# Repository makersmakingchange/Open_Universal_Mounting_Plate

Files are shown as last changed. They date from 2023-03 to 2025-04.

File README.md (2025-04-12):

#  Open Universal Mounting Plate
The Open Universal Mounting Plate is a simple mounting option for assistive devices that do not have integrated mounting hardware. This device uses hook and loop fastener strips to attach to an assistive device allowing it to be mounted with standard ¼”-20 mounts, like those found on readily available camera mounting accessories.

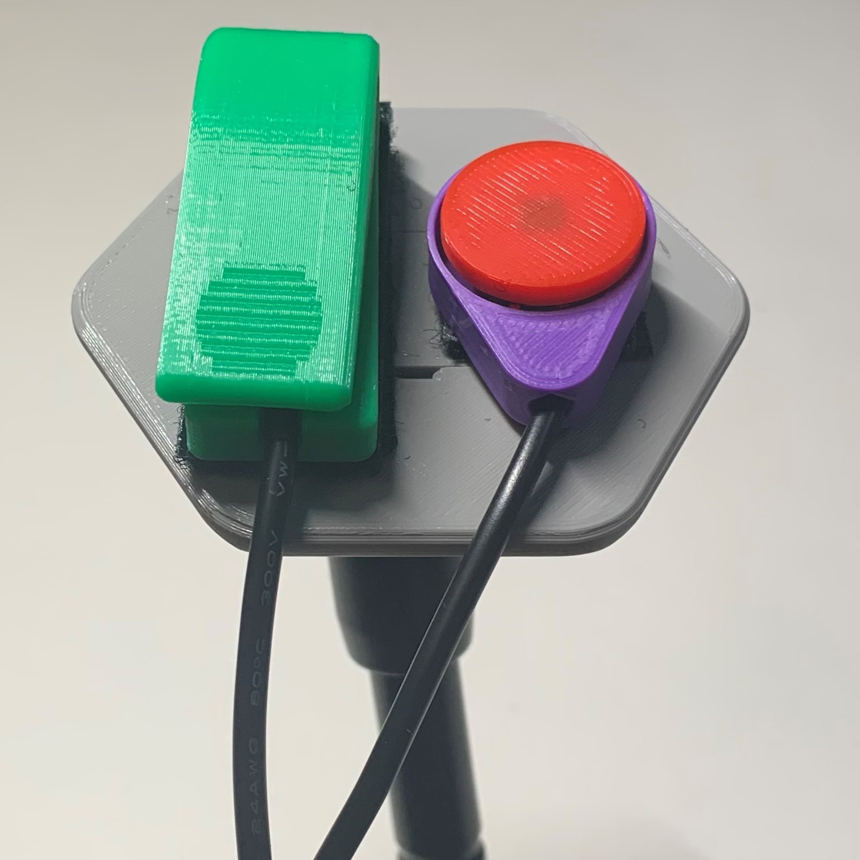
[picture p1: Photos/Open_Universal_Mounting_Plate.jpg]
A 3D printed hexagon mounting plate holding two assistive switches


## More info at
- [Makers Making Change Project Page](https://makersmakingchange.com/project/open-universal-mounting-plate)

## How to Obtain an Open Universal Mounting Plate
### 1. Do it Yourself (DIY) or Do it Together (DIT)

This is an open-source assistive technology, so anyone is free to build it. All of the files and instructions required to build the Open Universal Mounting Plate are contained within this repository. Refer to the Maker Checklist below.

### 2. Request a build of this device

If you would like to obtain an Open Universal Mounting Plate, you may submit a build request through the [MMC Library Page](https://makersmakingchange.com/project/open-universal-mounting-plate/). The requestor is responsible for the cost of materials and any shipping.

### 3. How to build this device for someone else

If you have the skills and equipment to build this device, and would like to donate your time to create the switch for someone who needs it, visit the [MMC Maker Wanted](https://makersmakingchange.com/maker-wanted/) section.

## Getting Started

### 1. Read the Makers Checklist

The Makers Checklist contains a list of tasks to complete to build the device.

### 2. Order the Off-The-Shelf Components

The [Bill of Materials](/Documentation/Open_Universal_Mounting_Plate_BOM.xlsx) lists all of the parts and components required to build the Open Universal Mounting Plate. The off-the-shelf components are are available online or may be available in smaller quantities at your local hardware store or dollar store.

### 3. Print the 3D Printable components

Refer to the [Sizing Chart](/Documentation/Open_Universal_Mounting_Plate_Sizing_Chart.pdf) to determine the correct configuration and corresponding print files.

All of the files and individual print files can be in the [/Build_Files/3D_Printing_Files](/Build_Files/3D_Printing_Files/) folder.

### 4. Assemble the Open Universal Mounting Plate...

Reference the [Assembly Guide](/Documentation/Open_Universal_Mounting_Plate_Assembly_Guide.pdf) for the tools and steps required to build each portion.

## Files
### Documentation
| Document             | Version | Link |
|----------------------|---------|------|
| Design Rationale     | 1.0     | [Open_Universal_Mounting_Plate_Design_Rationale](/Documentation/Open_Universal_Mounting_Plate_Design_Rationale.pdf)     |
| Maker Checklist      | 1.0     | [Open_Universal_Mounting_Plate_Maker_Checklist](/Documentation/Open_Universal_Mounting_Plate_Maker_Checklist.pdf)     |
| Bill of Materials    | 1.0     | [Open_Universal_Mounting_Plate_Bill_of_Materials](/Documentation/Open_Universal_Mounting_Plate_BOM.xlsx)     |
| 3D Printing Guide    | 1.0     | [Open_Universal_Mounting_Plate_3D_Printing_Guide](/Documentation/Open_Universal_Mounting_Plate_3D_Printing_Guide.pdf)     |
| Assembly Guide       | 1.0     | [Open_Universal_Mounting_Plate_Assembly_Guide](/Documentation/Open_Universal_Mounting_Plate_Assembly_Guide.pdf)     |
| User Guide           | 1.0     | [Open_Universal_Mounting_Plate_User_Guide](/Documentation/Open_Universal_Mounting_Plate_User_Guide.pdf)    |
| Sizing Chart         | 1.0     | [Open_Universal_Mounting_Plate_Sizing_Chart](/Documentation/Open_Universal_Mounting_Plate_Sizing_Chart.pdf)     |
| Changelog            | 1.0     | [Open_Universal_Mounting_Plate_Changelog](/Documentation/Open_Universal_Mounting_Plate_Changelog.pdf)     |

### Design Files
- [CAD Files](/Design_Files)

### Build Files
- [3D Printing Files](/Build_Files/3D_Printing_Files)

## Attribution

Design and documentation by Makers Making Change. 

## License
Everything needed or used to design, make, test, or prepare the Open Universal Mounting Plate is licensed under the CERN 2.0 Permissive license <https://ohwr.org/project/cernohl/wikis/Documents/CERN-OHL-version-2> (CERN-OHL-P) . 

Accompanying material such as instruction manuals, videos, and other copyrightable works that are useful but not necessary to design, make, test, or prepare the Open Universal Mounting Plate are published under a Creative Commons Attribution-ShareAlike 4.0 license https://creativecommons.org/licenses/by-sa/4.0/ (CC BY-SA 4.0).

---
<!-- ABOUT MMC START -->
## About Makers Making Change
[Makers Making Change Logo](https://www.makersmakingchange.com/)

Makers Making Change is a program of [Neil Squire](https://www.neilsquire.ca/), a Canadian non-profit that uses technology, knowledge, and passion to empower people with disabilities.

Makers Making Change leverages the capacity of community based Makers, Disability Professionals and Volunteers to develop and deliver affordable Open Source Assistive Technologies.

 - Website: [www.MakersMakingChange.com](https://www.makersmakingchange.com/)
 - GitHub: [makersmakingchange](https://github.com/makersmakingchange)
 - Bluesky: [@makersmakingchange.bsky.social](https://bsky.app/profile/makersmakingchange.bsky.social)
 - Instagram: [@makersmakingchange](https://www.instagram.com/makersmakingchange)
 - Facebook: [makersmakechange](https://www.facebook.com/makersmakechange)
 - LinkedIn: [Neil Squire Society](https://www.linkedin.com/company/neil-squire-society/)
 - Thingiverse: [makersmakingchange](https://www.thingiverse.com/makersmakingchange/about)
 - Printables: [MakersMakingChange](https://www.printables.com/@MakersMakingChange)

### Contact Us
For technical questions, to get involved, or to share your experience we encourage you to [visit our website](https://www.makersmakingchange.com/) or [contact us](https://www.makersmakingchange.com/s/contact).
<!-- ABOUT MMC END -->

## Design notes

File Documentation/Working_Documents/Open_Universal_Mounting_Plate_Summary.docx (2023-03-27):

Title

Open Universal Mounting Plate

Subtitle

A simple mounting option for AT that doesn’t have integrated mounting hardware.

## Device Specifications

Build Time:

< 1hr

1-4 hr

5-10hr

>10hr

Cost:

$0 - $10

$11 - $25

$26 - $50

$51 - $100

$101 - $250

$250+

Stage: Recently Added

Skills: 3D Printing

Need: Agility / Dexterity

Disability: Mobility / Physical

Difficulty: Beginner

License:

Usages:

Type:

Designer:

## Device Details

### Overview

The Open Universal Mounting Plate is a simple mounting option for assistive devices that do not have integrated mounting hardware. This device uses hook and loop fastener strips to attach to an assistive device allowing it to be mounted with standard ¼”-20 mounts, like those found on readily available camera mounting accessories.

### Sizing

This device has multiple options for both mounting plate size and tee nut length. If you are requesting this device, please let the builder know what options work best for you. Refer to the Sizing Chart for more information.

### Usage

Hook and loop fastener strips (Velcro) can be used to secure one or more devices to the mounting plate. A mounting system that uses ¼”-20 external threads can then me secured to the mounting and positioned for use.

### Cost

~

### Build Instructions

Refer to the Assembly Guide and 3D Printing Guide for detailed instructions.

#### Skills Required

This is a beginner level build that involves 3D printing and minor assembly.

#### Time Required

3D Printing Time: 1h24m to 4h14m (depending on plate size and tee nut length)

Assembly Time: 15m

#### Tools

- 3D Printer
- Small Flat Head Screwdriver
- Pliers

#### Components

- 1X Mounting Plate
- 1X Hardware Cover
- 1X Assembly Washer

### Attribution

Design and Documentation by Makers Making Change

© 2022 by <Author>. This work is licensed under the CC BY SA 4.0 License: http://creativecommons.org/licenses/by-sa/4.0 Files available at <Replace with MMC Library Link> Page 1 of 2

VX.X | <MONTH> <YEAR> <Device Name> Summary

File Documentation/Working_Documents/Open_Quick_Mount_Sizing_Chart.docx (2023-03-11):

# Introduction

The Hexagon Quick Mount is a simple mounting option for assistive devices that do not have integrated mounting hardware. This device has multiple options for both mounting plate size and tee nut length. If you are requesting this device, please let the builder know what options work best for you.

## Using this Sizing Chart

The sizing chart can be printed on standard letter sized paper (8.5” x 11”) to help determine the best options based on the devices you wish to mount. Do not use setting such as “Fit to page” that will alter the correct sizing of the following diagrams.

### Choosing a Mounting Plate Size

Arrange the device(s) you wish to mount onto the following diagram to determine what size works best for your application. There are three sizes available with widths of 45 mm, 65 mm, and 85 mm.

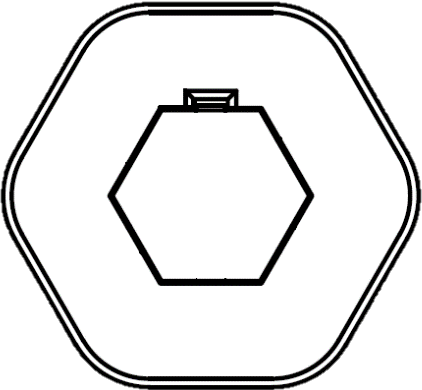
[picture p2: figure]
Scaled drawing of the small hexagon mounting plate.
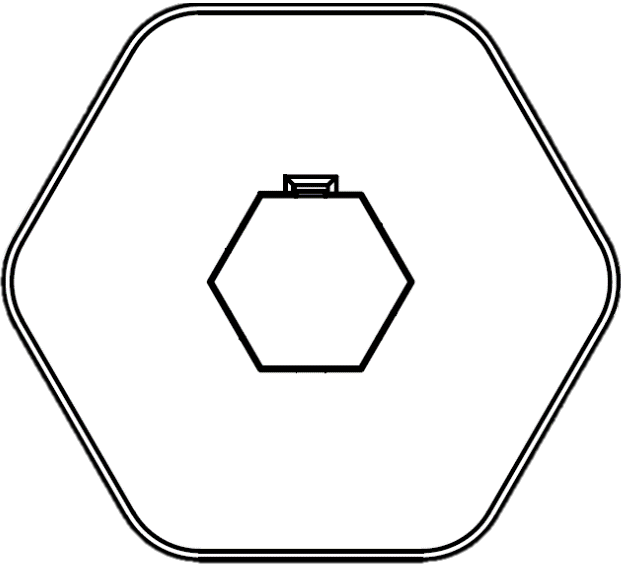
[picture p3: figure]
Scaled drawing of the medium hexagon mounting plate.

Small Plate

Medium Plate

Large Plate

85 mm

65 mm

45 mm

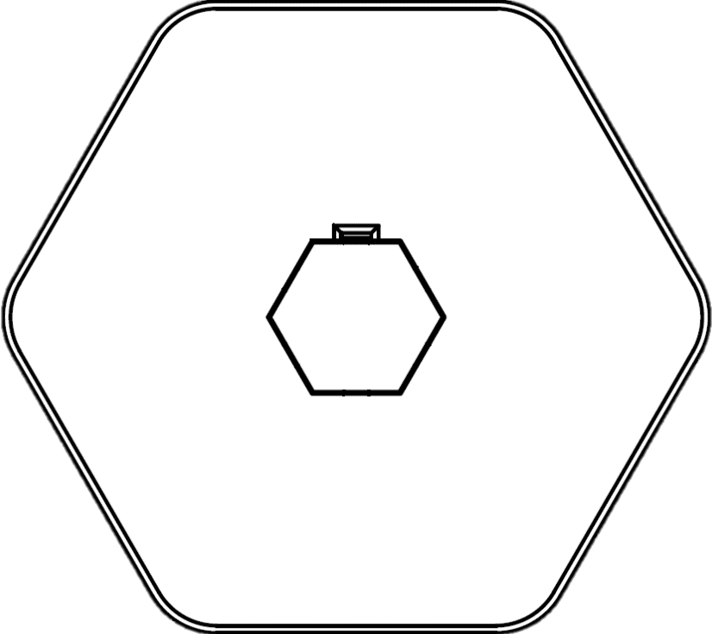
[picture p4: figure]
Scaled drawing of the large hexagon mounting plate.

### Choosing a Tee Nut Length

The length of tee nut determines the approximate length of threads available for attaching the mounting plate to a mounting system. If you have a tee nut size preference, let the builder know. Otherwise, the following diagram is intended to let builders easily identify their tee nut size. Place your tee nut onto the diagram below to verify what length tee you are using.

| Tee Nut Options
| 5/16” x ¼"-20 UNC | 7/16” x ¼"-20 UNC | 9/16” x ¼"-20 UNC

### Selecting The Correct Print File

Once you have determined your mounting plate size and tee nut length, use the following table to find the correct print file name.

Print File Name | Mounting Plate Size | Tee Nut
45_Mounting_Plate_5.stl | 45 mm | 5/16” x ¼"-20 UNC
45_Mounting_Plate_5.stl | 45 mm | 7/16” x ¼"-20 UNC
45_Mounting_Plate_5.stl | 45 mm | 9/16” x ¼"-20 UNC
65_Mounting_Plate_7.stl | 65 mm | 5/16” x ¼"-20 UNC
65_Mounting_Plate_7.stl | 65 mm | 7/16” x ¼"-20 UNC
65_Mounting_Plate_7.stl | 65 mm | 9/16” x ¼"-20 UNC
85_Mounting_Plate_9.stl | 85 mm | 5/16” x ¼"-20 UNC
85_Mounting_Plate_9.stl | 85 mm | 7/16” x ¼"-20 UNC
85_Mounting_Plate_9.stl | 85 mm | 9/16” x ¼"-20 UNC

© 2023 by Neil Squire This work is licensed under the CC BY SA 4.0 License: http://creativecommons.org/licenses/by-sa/4.0 Files available at <Replace with MMC Library Link> Page 1 of 1

V1.0 | February 2023 <Device Name> Sizing chart

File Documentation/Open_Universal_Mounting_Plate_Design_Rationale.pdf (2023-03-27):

V1.0 | February 2023

## Open Universal Mounting Plate

## DESIGN RATIONALE

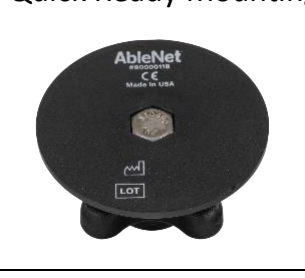
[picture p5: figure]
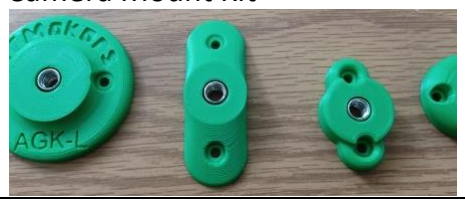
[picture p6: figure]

© 2023 by Neil Squire (https://neilsquire.ca/)
This work is licensed under the CC BY SA 4.0 License: http://creativecommons.org/licenses/by-sa/4.0
Files available at Files available at https://makersmakingchange.com/project/open-universal-mounting-plate | Page 1 of 12

### Introduction

The Open Universal Mounting Plate is a simple mounting option for assistive devices that do not have integrated mounting hardware. This device uses hook and loop fastener strips to attach to an assistive device allowing it to be mounted with standard ¼”-20 mounts, like those found on readily available camera mounting accessories.

### Research

### Commercial Products

Device | Cost | Notes | Link
Quick Ready Mounting Plate | $35 | This device uses hook and loop fastener strips to secure an assistive device to a mounting plate. The mounting plate has an attached external ¼”-20 bolt to allow the device to be mounted. | https://www.ablenetinc.com/quick-ready-mounting-plate-for-assistive-technology/ (https://www.ablenetinc.com/quick-ready-mounting-plate-for-assistive-technology/)
Quick Release Plate | $43 | This device uses rails that match the geometry of another device to secure ¼ -20 threads to for mounting. | FALCAM F38 Quick Release Plate (https://www.amazon.ca/Release-Universal-Mounting-Aluminum-Stabilizer/dp/B092S2SFLM)

### DIY Designs

Device | Cost | Notes | Link
Camera Mount Kit | ~$26 for 12 | Various bolt on adapters that allow you to add internal ¼”-20 threads to a device. Uses screws to mount to the device. | Camera Mount Adapters for the Logitech Adaptive Gaming Kit -Makers Making Change (https://makersmakingchange.com/project/camera-mount-adapters-for-the-logitech-adaptive-gaming-kit/)
Suction-Cup Switch Mount | ~$10 | This mount attaches to AT with hook and loop fastener and uses a section cup for mounting. Must be mounted to smooth flat surfaces. | Suction-Cup Switch Mount -Makers Making Change (https://makersmakingchange.com/project/suction-cup-switch-mount/)

## DESIGN RATIONALE

Files available at Files available at https://makersmakingchange.com/project/open-universal-mounting-plate | Page 2 of 12

### Requirements

### Goals

G01 Securely mount AT that doesn’t have integrated mounts

### Functional Requirements

F01 | Must be compatible with standard AT mounts (1/4”-20 UNC)
F02 | Must be able to hold the weight of small AT (XX g)
F03 | Must allow approximately 5 mm of threads to be engaged for mounting. (Or standard number of thread engagement)

### Non-functional Requirement

NF01 | Multiple mounting plate size options
NF02 | The device must be able to accommodate three lengths of ¼+-20 UNC tee nuts: 5/16”, 7/16”, and 9/16”.

### Constraints

C01 | Easily printable with common maker printers
C02 | No specialty tools for assembly
C03 | Use easily available, off the shelf parts

### Ideation

### Threaded Mounting Connections

The mounting plate is intended to attach to a mounting system with a threaded connection. Mounting systems are available with either external threads or internal threads. DIY and camera mounting systems typically have an external thread, such as the magic arm (e.g., SmallRig Articulating Magic Arm). (https://www.amazon.com/SmallRig-Adjustable-Friction-Articulating-Monitor/dp/B087T4T8D5) There are also AT-specific mounting systems that have an internal thread (e.g., the AbleNet One Mount (https://www.ablenetinc.com/one/) ).

Connection Type | Mounting System | Mounting Plate | Comments
Internal-External | Internal Thread | External Thread | No additional hardware required.
Internal-Internal | Internal Thread | Internal Thread | This could possibly be achieved with a male-to-male thread adapter.
External-External | External Thread | External Thread | This can be achieved with a coupling nut. Coupling nuts are readily available and inexpensive.
External-Internal | External Thread | Internal Thread | No additional hardware required.

## DESIGN RATIONALE

Files available at Files available at https://makersmakingchange.com/project/open-universal-mounting-plate | Page 3 of 12

Threaded Connection Mounting Option 1: Internal Threads
An internal threaded connection (i.e., female) provides the ability to connecting to a mounting system with an external (I.e., male) thread.

There are several ways that an internal threaded connection can be added to a 3D printed part:

1. 3D printed threads.
2. Tapped threads.
3. Integrated hardware
a. Hex nut
b. Tee nut
c. Heat-set insert.

Threaded Connection Mounting Option 2: External Threads
An external threaded connection (I.e., male) provides the ability to connect to a mounting system with an internal (i.e., female) thread. A mounting knob is commonly used to fix this connection in a desired orientation.

Some ways external threaded connections can be added to a 3D printed part:

1. 3D printed threads (size and print orientation will be important for strength)
2. Hex Bolt

Threaded Connection Mounting Option 3: Combined Internal-External Threads
The third option is a design that provides both an internal and external threaded connection or the ability to easily swap between configurations.

Some ways external and internal threaded connections can be added to a 3D printed part:

1. Modular design that can be swapped out.
2. Use of a tee nut and hex bolt
a. Internal threads: Only the tee nut is used.
b. External threads: A hex bolt is threaded through the tee nut to expose external threads.

## DESIGN RATIONALE

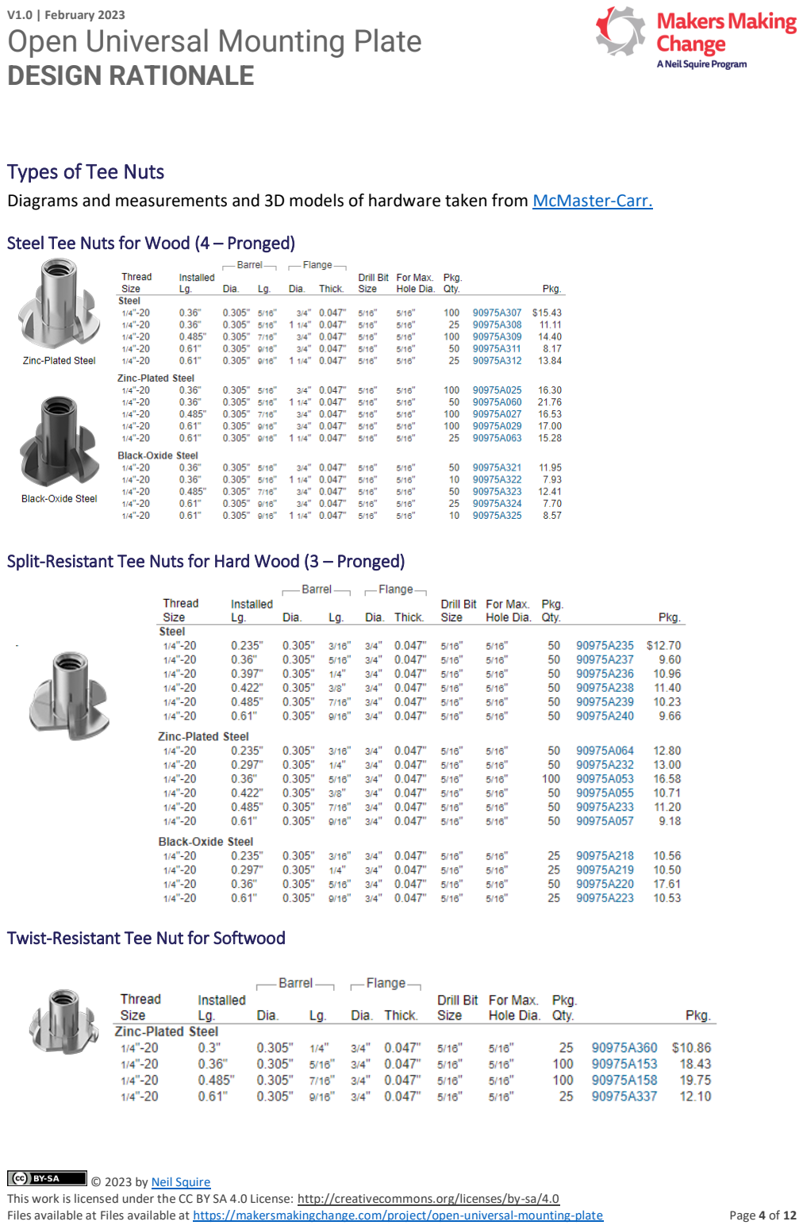
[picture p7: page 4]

Files available at Files available at https://makersmakingchange.com/project/open-universal-mounting-plate | Page 4 of 12

### Types of Tee Nuts

Diagrams and measurements and 3D models of hardware taken from McMaster-Carr. (https://www.mcmaster.com/tee-nuts/thread-size~1-4-20/)

Steel Tee Nuts for Wood (4 – Pronged)

Split-Resistant Tee Nuts for Hard Wood (3 – Pronged)

Twist-Resistant Tee Nut for Softwood

## DESIGN RATIONALE

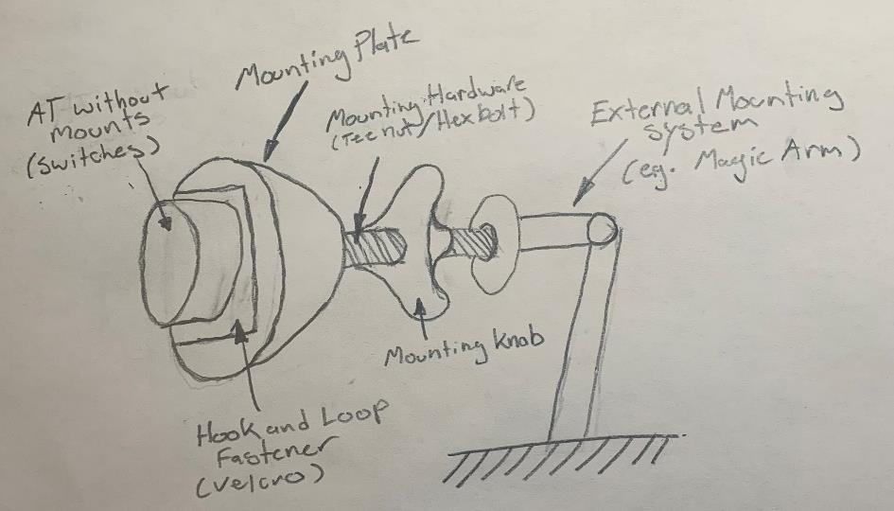
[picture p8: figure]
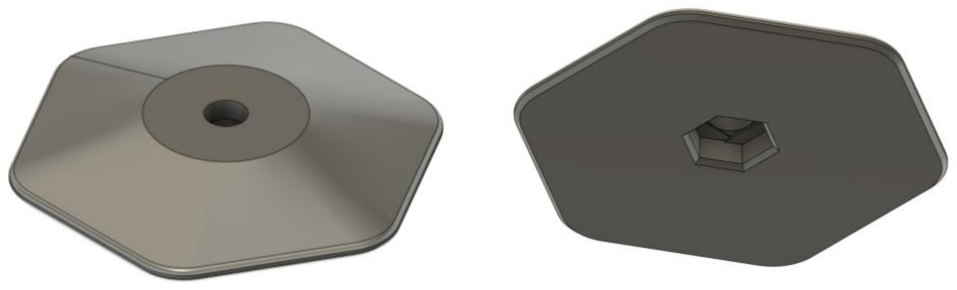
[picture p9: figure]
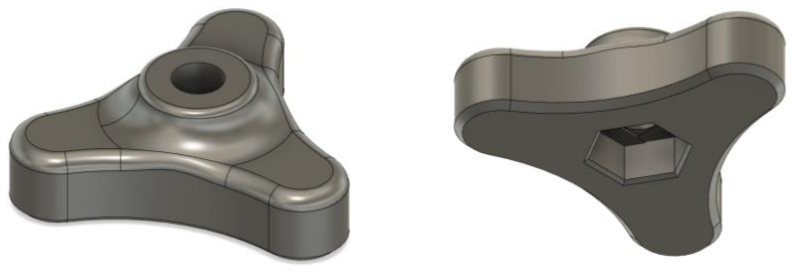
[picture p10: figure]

Files available at Files available at https://makersmakingchange.com/project/open-universal-mounting-plate | Page 5 of 12

### Conceptual Design

### Initial Concept

### Hexagon Mounting Plate (External ¼”-20 Threads)

Notes: This design attaches a ¼”-20 hex bolt to a mounting plate. To increase the adaptability of this design, a ¼”-20 T-nut could be added so internal threads can also be used for mounting.

Mounting Knob with ¼” – 20 nut recess.

Notes: Can only apply force in one direction. A captive nut would allow this knob to apply force in both directions depending on the use.

## DESIGN RATIONALE

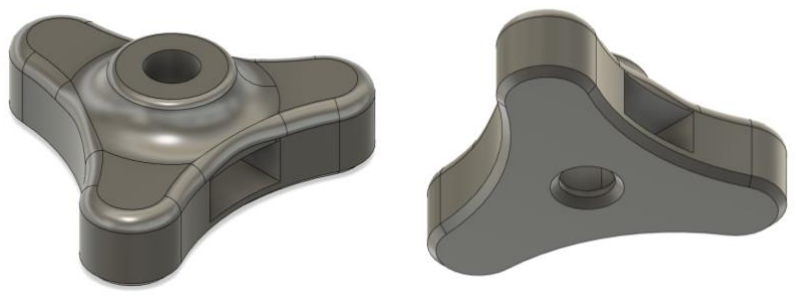
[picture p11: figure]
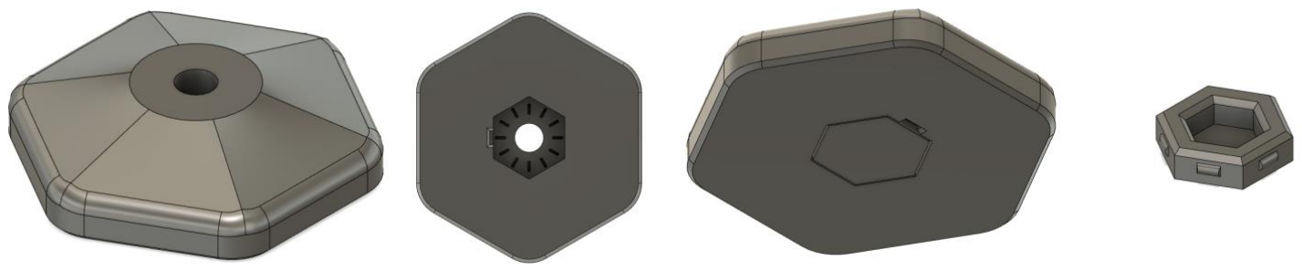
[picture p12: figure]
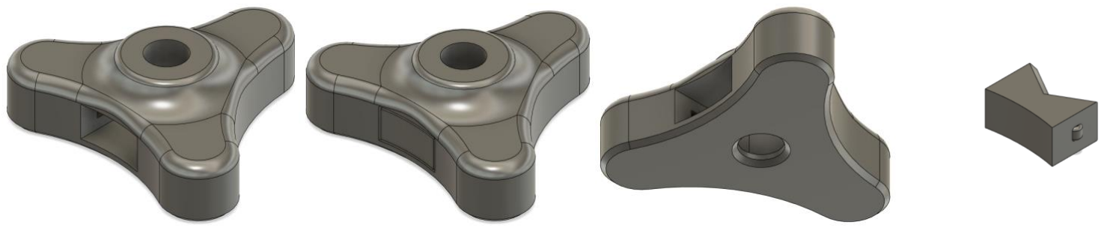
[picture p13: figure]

Files available at Files available at https://makersmakingchange.com/project/open-universal-mounting-plate | Page 6 of 12

Mounting Knob with captured ¼” – 20 nuts.

Notes: Sacrificial bridges used to make this printable without supports but a cover should be added to keep the bolt hole from interfering with the user.

### Prototyping

### Parametric Mounting Plate with Mounting Knob

This prototype has increased thickness allowing room for a tee nut and a hex bolt to be installed and hidden via a snap fit cover. If the user wishes to use internal threads for mounting, the hex bolt can be removed and only the tee nut used. If external threads are required, the hex bolt can be threaded through the tee nut from the bottom. The cover is used to cover the internal hardware and keep the hex bolt from rotating inside when used. The cover can be popped out via a small screwdriver.

When using the external threads of the hex bolt, it is common to use a mounting knob to secure the device in the desired orientation.

## DESIGN RATIONALE

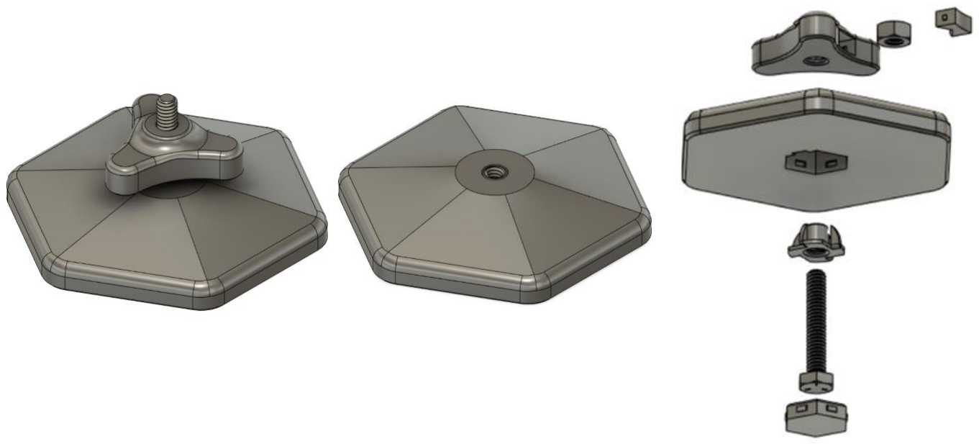
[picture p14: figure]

Files available at Files available at https://makersmakingchange.com/project/open-universal-mounting-plate | Page 7 of 12

### Prototype Assembly

### Detailed Design

### Design Decisions

Mounting Plate Size Options
The sizes and shapes of MCC switches without integrated mounts will be considered to determine appropriate mounting plate sizes.
Existing MCC Switches | Dimensions of Base (mm) | Shape | Integrated ¼”-20 Mounts
Interact Switch | 85 x 85 | Round | N
Raindrop | 30 x 20 | Rectangular | N
Light Touch | 50 x 20 | Rectangular | N
MCC 60 | 60 x 60 | Round | Y
Solderless Uni Body | 50 x 20 | Rectangular | N
Round Touch 60 | 60 x 60 | Round | N
Low Profile Switch | 65 x 65 | Square | N

## DESIGN RATIONALE

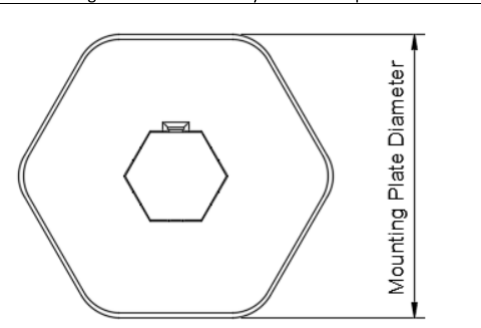
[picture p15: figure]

Files available at Files available at https://makersmakingchange.com/project/open-universal-mounting-plate | Page 8 of 12

Mounting Plate Size Selection
Three sizes were selected: 45 mm, 65 mm, and 85 mm.
Plate Size | Consideration
Small – 45 mm | • Smaller than commercial alternative • Allows one or two smaller switches to be mounted
Medium – 65 mm | • Comparable size to commercial universal mounts • Allows up to three raindrop / light touch switches to me mounted side by side. • Ideal for mid-sized switches
Large – 85 mm | • Larger than commercial alternative • Can mount the larger MCC switches (Interact switch) • Enough room for various layouts of multiple small switches

Threaded Connection Type (Internal/External)
There are three options for threaded connection on the mount: internal, external, and combined internal/external.

Threaded Connection Selection
The prototype was designed to provide both internal (tee nut) and external (hex bolt) mounting options. To reduce complexity and material cost, only internal threads (tee nut) will be integrated. Internal threads for mounting are a more common method of mounting that MMC uses. This reduces the thickness of the plate, resulting in reduced print time, and eliminates the need for the mounting knob.

## DESIGN RATIONALE

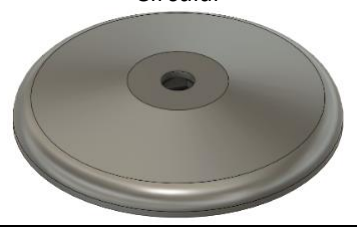
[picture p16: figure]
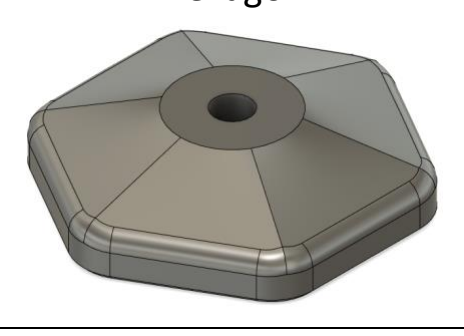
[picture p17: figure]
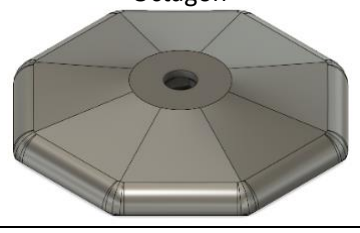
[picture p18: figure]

Files available at Files available at https://makersmakingchange.com/project/open-universal-mounting-plate | Page 9 of 12

Mounting Plate Shape
Shape Considered | Notes
Circular | • Like other mounting plate options. • No sharp corners. • Matches shape of circular assistive switches
Hexagon | • Differs from existing mounting options. • Flat edges give better grip for mounting. • Edges can be rounded to reduce sharpness.
Octagon | • Similar advantages to the hexagon in style and grip.

Mounting Plate Shape Selection: Hexagon Plate
We will continue with the hexagon shaped plate used in the prototype device.

The tee nut mount and cover without a mounting plate will be offered for designers that wish to create their own plate size and shape.

Tee Nut Sizes
Ideally, there will be alternate versions of this device to match the size and style of T-Nuts that the builder has on hand. Due to the vast number of different sizes, only 3-4 of the most common types will be focused on and a parametric Fusion 360 model will be available for builders to match any size of hardware.

## DESIGN RATIONALE

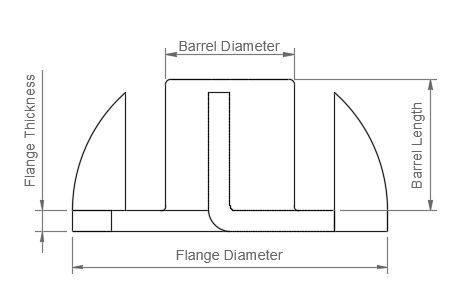
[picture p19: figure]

Files available at Files available at https://makersmakingchange.com/project/open-universal-mounting-plate | Page 10 of 12

Tee Nut Size Selection
The design will accommodate a limited set of the most commonly available tee nut sizes.
Tee Nut Option | Specification | Barrel Diameter [mm] (in) | Barrel Length [mm] (in) | Flange Thickness [mm] (in) | Flange Diameter [mm] (in) | # of Prongs
1 | 5/16” x ¼"-20 UNC | 7.75 (0.305) | 7.94 (5/16) | 1.194 (0.047) | 19.05 (3/4) | 3, 4, 6
2 | 7/16” x ¼"-20 UNC | 7.75 (0.305) | 11.11 (7/16) | 1.194 (0.047) | 19.05 (3/4) | 3, 4, 6
3 | 9/16” x ¼"-20 UNC | 7.75 (0.305) | 14.29 (9/16) | 1.194 (0.047) | 19.05 (3/4) | 3, 4, 6

Standard Configurations
A set of standard configurations will be released as individual print files to make it easier to print the device for the desired mounting plate size and tee nut hardware. The print files released will be constrained to 3 different plate widths that will accept 3 of the most commonly available sizes of tee nuts.
Name | Mounting Plate Size | Shape | Tee Nut
OUP-45-H-5 | 45 mm | Hexagon | 5/16”
OUP-45-H-7 | 45 mm | Hexagon | 7/16”
OUP-45-H-9 | 45 mm | Hexagon | 9/16”
OUP-65-H-5 | 65 mm | Hexagon | 5/16”

## DESIGN RATIONALE

Files available at Files available at https://makersmakingchange.com/project/open-universal-mounting-plate | Page 11 of 12
OUP-65-H-7 | 65 mm | Hexagon | 7/16”
OUP-65-H-9 | 65 mm | Hexagon | 9/16”
OUP-85-H-5 | 85 mm | Hexagon | 5/16”
OUP-85-H-7 | 85 mm | Hexagon | 7/16”
OUP-85-H-9 | 85 mm | Hexagon | 9/16”

### Device Name

- Open Universal Mount
- Open Quick Mount
- Universal AT Mount
- Hexagon Universal Mounting Plate
- Hexagon Quick Mount
- Universal Hexagon Mount
- Open Universal Mounting Plate

### Testing

Print Test
The Tee Nut Mount (without mounting plate) was tested on another printer.
- Tee Nut Installation
- Some difficulty installing tee nut due to sacrificial bridge.
- Successfully installed.
- Hardware Cover Installation
- Found that the cover could be installed too deep and sit crooked.
- Didn’t have this issue once the tee nut was installed.
- Overall Notes
- No major concerns.

Snap Fit Cover Durability
The hardware cover can be removed to expose the tee nut used for mounting. The durability of this part is less of a concern now that only internal threads are offered and there is no need to replace the mounting hardware for external threads.

## DESIGN RATIONALE

Files available at Files available at https://makersmakingchange.com/project/open-universal-mounting-plate | Page 12 of 12

### Opportunities for Improvement

1. Provide the option for external mounting threads.
2. Modular Tee Nut mount that can connect to any of the plate sizes.

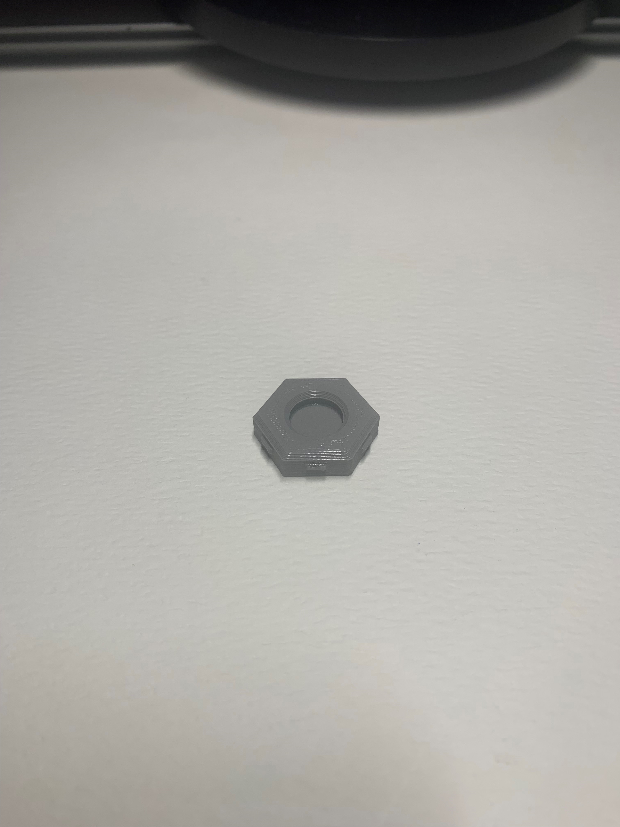
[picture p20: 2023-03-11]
Photos/Print_Photos/Hardware_Cover_Back.jpg

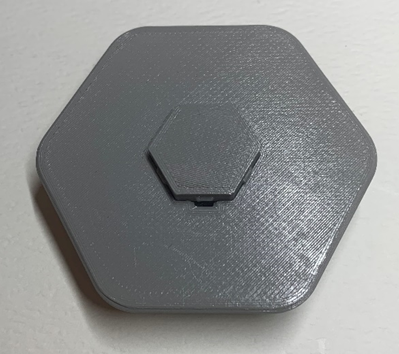
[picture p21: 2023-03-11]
Photos/Assembly_Photos/Hardware_Cover_Aligned.png

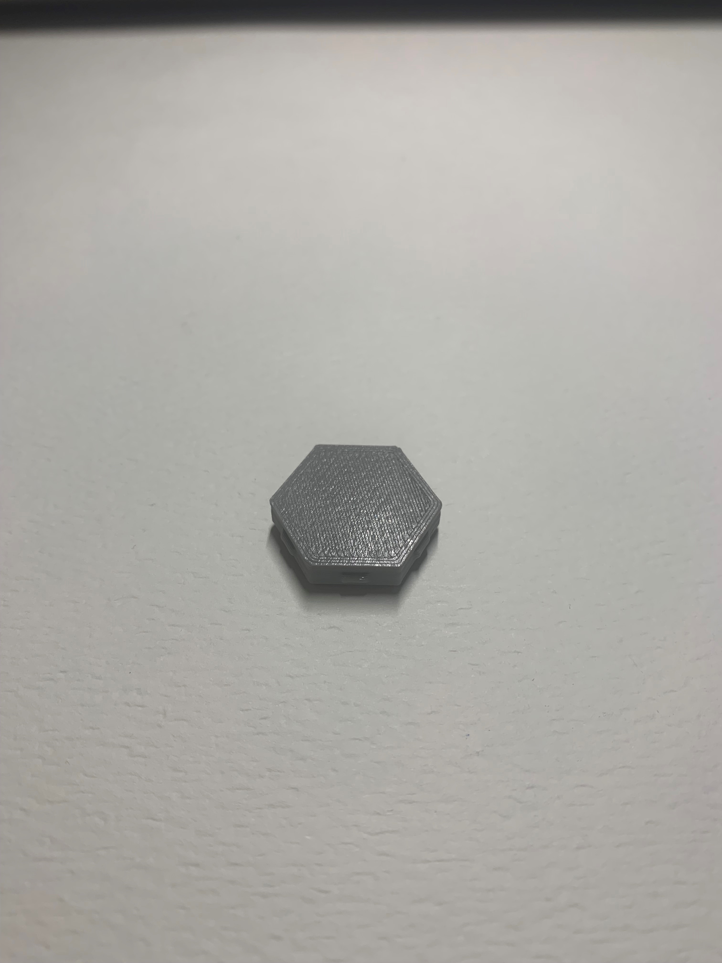
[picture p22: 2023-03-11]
Photos/Print_Photos/Hardware_Cover_Front.jpg

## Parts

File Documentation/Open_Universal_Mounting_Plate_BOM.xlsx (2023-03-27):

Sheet: BOM_S_5-16
Open Universal Mounting Plate - Small Plate - 5/16 Tee Nut |  |  |  |  |  |  |  | Unit Cost | Total Cost | Total Print time (hr) | Total filament (g)
Version: V1.0 |  | Last Updated: 2023-Feb-27 |  |  |  |  |  | $3.06 | $3.06 | 1.32 | 11
Commercial Parts |  | Ensure to select the correct spreadsheet for your configoration
ID | Part Name | Part Type | QTY | QTY/PKG | $/PKG | PKG QTY | $/Unit | Extended | Total | Link
 | 5/16" x 1/4"-20 UNC Tee Nut | Fastener | 1 | 1 | $2.79 | 1 | $2.79 | $2.79 | $2.79 | Hillman Tee Nuts, Zinc | Canadian Tire
3D Printed Parts ESTIMATED PRICING USING 1KG ROLL COST: |  | $25.00
ID | Part | Material | QTY | Mass (g) / Unit | Time / Unit |  | Print Time (Min) | Estimated Price |  | Link
 | 45_Mounting_Plate_5.stl | PLA | 1 | 9 | 69 |  | $69.00 | $0.22
 | Hardware_Cover.stl | PLA | 1 | 1 | 10 |  | 10 | $0.03
 | Assembly_Washer.stl | PLA | 1 | 1 | 5 |  | 5 | $0.03
Custom Printed Circuit Board (PCB)
ID | Part |  | QTY
Tools for Assembly
 | Pliers
 | Small Screw Driver
 | 1/4"-20 UNC Bolt (Optional)
Alternatives (if there are other sources for some parts link them below)
ID | Part and description |  |  |  |  |  |  |  |  | Link
 | 5/16" x 1/4"-20 UNC Tee Nut Insert |  | 1 | 100 | $15.43 | 1 | $0.15 |  |  | Steel Tee Nut Inserts, 1/4"-20 Size, 0.36" Installed Length, 3/4" Flange Diameter | McMaster-Carr (https://www.mcmaster.com/90975A307/)
 | 7/16" x 1/4"-20 UNC Tee Nut Insert |  | 1 | 100 | $14.40 | 1 | $0.14 |  |  | Steel Tee Nut Inserts, 1/4"-20 Size, 0.485" Installed Length, 3/4" Flange Diameter | McMaster-Carr (https://www.mcmaster.com/90975A309/)
 | 9/16" x 1/4"-20 UNC Tee Nut Insert |  | 1 | 50 | $8.17 | 1 | $0.16 |  |  | Steel Tee Nut Inserts, 1/4"-20 Size, 0.61" Installed Length, 3/4" Flange Diameter | McMaster-Carr (https://www.mcmaster.com/90975A311/)

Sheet: BOM_S_7-16
Open Universal Mounting Plate - Small Plate - 7/16 Tee Nut |  |  |  |  |  |  |  | Unit Cost | Total Cost | Total Print time (hr) | Total filament (g)
Version: V1.0 |  | Last Updated: 2023-Feb-27 |  |  |  |  |  | $0.44 | $14.70 | 1.38 | 12
Commercial Parts |  | Ensure to select the correct spreadsheet for your configoration
ID | Part Name | Part Type | QTY | QTY/PKG | $/PKG | PKG QTY | $/Unit | Extended | Total | Link
 | 7/16" x 1/4"-20 UNC Tee Nut | Fastener | 1 | 100 | $14.40 | 1 | $0.14 | $0.14 | $14.40 | Steel Tee Nut Inserts, 1/4"-20 Size, 0.485" Installed Length, 3/4" Flange Diameter | McMaster-Carr
3D Printed Parts ESTIMATED PRICING USING 1KG ROLL COST: |  | $25.00
ID | Part | Material | QTY | Mass (g) / Unit | Time / Unit |  | Print Time (Min) | Estimated Price |  | Link
 | 45_Mounting_Plate_7.stl | PLA | 1 | 10 | 73 |  | $73.00 | $0.25
 | Hardware_Cover.stl | PLA | 1 | 1 | 10 |  | 10 | $0.03
 | Assembly_Washer.stl | PLA | 1 | 1 | 5 |  | 5 | $0.03
Custom Printed Circuit Board (PCB)
ID | Part |  | QTY
Tools for Assembly
 | Pliers
 | Small Screw Driver
 | 1/4"-20 UNC Bolt (Optional)
Alternatives (if there are other sources for some parts link them below)
ID | Part and description |  |  |  |  |  |  |  |  | Link
 | 5/16" x 1/4"-20 UNC Tee Nut Insert |  | 1 | 100 | $15.43 | 1 | $0.15 |  |  | Steel Tee Nut Inserts, 1/4"-20 Size, 0.36" Installed Length, 3/4" Flange Diameter | McMaster-Carr (https://www.mcmaster.com/90975A307/)
 | 7/16" x 1/4"-20 UNC Tee Nut Insert |  | 1 | 100 | $14.40 | 1 | $0.14 |  |  | Steel Tee Nut Inserts, 1/4"-20 Size, 0.485" Installed Length, 3/4" Flange Diameter | McMaster-Carr (https://www.mcmaster.com/90975A309/)
 | 9/16" x 1/4"-20 UNC Tee Nut Insert |  | 1 | 50 | $8.17 | 1 | $0.16 |  |  | Steel Tee Nut Inserts, 1/4"-20 Size, 0.61" Installed Length, 3/4" Flange Diameter | McMaster-Carr (https://www.mcmaster.com/90975A311/)

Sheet: BOM_S_9-16
Open Universal Mounting Plate - Small Plate - 9/16 Tee Nut |  |  |  |  |  |  |  | Unit Cost | Total Cost | Total Print time (hr) | Total filament (g)
Version: V1.0 |  | Last Updated: 2023-Feb-27 |  |  |  |  |  | $0.49 | $8.49 | 1.48 | 13
Commercial Parts |  | Ensure to select the correct spreadsheet for your configoration
ID | Part Name | Part Type | QTY | QTY/PKG | $/PKG | PKG QTY | $/Unit | Extended | Total | Link
 | 9/16" x 1/4"-20 UNC Tee Nut | Fastener | 1 | 50 | $8.17 | 1 | $0.16 | $0.16 | $8.17 | Steel Tee Nut Inserts, 1/4"-20 Size, 0.61" Installed Length, 3/4" Flange Diameter | McMaster-Carr
3D Printed Parts ESTIMATED PRICING USING 1KG ROLL COST: |  | $25.00
ID | Part | Material | QTY | Mass (g) / Unit | Time / Unit |  | Print Time (Min) | Estimated Price |  | Link
 | 45_Mounting_Plate_9.stl | PLA | 1 | 11 | 79 |  | $79.00 | $0.27
 | Hardware_Cover.stl | PLA | 1 | 1 | 10 |  | 10 | $0.03
 | Assembly_Washer.stl | PLA | 1 | 1 | 5 |  | 5 | $0.03
Custom Printed Circuit Board (PCB)
ID | Part |  | QTY
Tools for Assembly
 | Pliers
 | Small Screw Driver
 | 1/4"-20 UNC Bolt (Optional)
Alternatives (if there are other sources for some parts link them below)
ID | Part and description |  |  |  |  |  |  |  |  | Link
 | 5/16" x 1/4"-20 UNC Tee Nut Insert |  | 1 | 100 | $15.43 | 1 | $0.15 |  |  | Steel Tee Nut Inserts, 1/4"-20 Size, 0.36" Installed Length, 3/4" Flange Diameter | McMaster-Carr (https://www.mcmaster.com/90975A307/)
 | 7/16" x 1/4"-20 UNC Tee Nut Insert |  | 1 | 100 | $14.40 | 1 | $0.14 |  |  | Steel Tee Nut Inserts, 1/4"-20 Size, 0.485" Installed Length, 3/4" Flange Diameter | McMaster-Carr (https://www.mcmaster.com/90975A309/)
 | 9/16" x 1/4"-20 UNC Tee Nut Insert |  | 1 | 50 | $8.17 | 1 | $0.16 |  |  | Steel Tee Nut Inserts, 1/4"-20 Size, 0.61" Installed Length, 3/4" Flange Diameter | McMaster-Carr (https://www.mcmaster.com/90975A311/)

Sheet: BOM_M_5-16
Open Universal Mounting Plate - Medium Plate - 5/16 Tee Nut |  |  |  |  |  |  |  | Unit Cost | Total Cost | Total Print time (hr) | Total filament (g)
Version: V1.0 |  | Last Updated: 2023-Feb-27 |  |  |  |  |  | $3.26 | $3.27 | 2.40 | 19
Commercial Parts |  | Ensure to select the correct spreadsheet for your configoration
ID | Part Name | Part Type | QTY | QTY/PKG | $/PKG | PKG QTY | $/Unit | Extended | Total | Link
 | 5/16" x 1/4"-20 UNC Tee Nut | Fastener | 1 | 1 | $2.79 | 1 | $2.79 | $2.79 | $2.79 | Hillman Tee Nuts, Zinc | Canadian Tire
3D Printed Parts ESTIMATED PRICING USING 1KG ROLL COST: |  | $25.00
ID | Part | Material | QTY | Mass (g) / Unit | Time / Unit |  | Print Time (Min) | Estimated Price |  | Link
 | 65_Mounting_Plate_5.stl | PLA | 1 | 17 | 134 |  | $134.00 | $0.43
 | Hardware_Cover.stl | PLA | 1 | 1 | 10 |  | 10 | $0.03
 | Assembly_Washer.stl | PLA | 1 | 1 | 5 |  | 5 | $0.03
Custom Printed Circuit Board (PCB)
ID | Part |  | QTY
Tools for Assembly
 | Pliers
 | Small Screw Driver
 | 1/4"-20 UNC Bolt (Optional)
Alternatives (if there are other sources for some parts link them below)
ID | Part and description |  |  |  |  |  |  |  |  | Link
 | 5/16" x 1/4"-20 UNC Tee Nut Insert |  | 1 | 100 | $15.43 | 1 | $0.15 |  |  | Steel Tee Nut Inserts, 1/4"-20 Size, 0.36" Installed Length, 3/4" Flange Diameter | McMaster-Carr (https://www.mcmaster.com/90975A307/)
 | 7/16" x 1/4"-20 UNC Tee Nut Insert |  | 1 | 100 | $14.40 | 1 | $0.14 |  |  | Steel Tee Nut Inserts, 1/4"-20 Size, 0.485" Installed Length, 3/4" Flange Diameter | McMaster-Carr (https://www.mcmaster.com/90975A309/)
 | 9/16" x 1/4"-20 UNC Tee Nut Insert |  | 1 | 50 | $8.17 | 1 | $0.16 |  |  | Steel Tee Nut Inserts, 1/4"-20 Size, 0.61" Installed Length, 3/4" Flange Diameter | McMaster-Carr (https://www.mcmaster.com/90975A311/)

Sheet: BOM_M_7-16
Open Universal Mounting Plate - Medium Plate - 7/16 Tee Nut |  |  |  |  |  |  |  | Unit Cost | Total Cost | Total Print time (hr) | Total filament (g)
Version: V1.0 |  | Last Updated: 2023-Feb-27 |  |  |  |  |  | $0.67 | $14.93 | 2.30 | 21
Commercial Parts |  | Ensure to select the correct spreadsheet for your configoration
ID | Part Name | Part Type | QTY | QTY/PKG | $/PKG | PKG QTY | $/Unit | Extended | Total | Link
 | 7/16" x 1/4"-20 UNC Tee Nut | Fastener | 1 | 100 | $14.40 | 1 | $0.14 | $0.14 | $14.40 | Steel Tee Nut Inserts, 1/4"-20 Size, 0.485" Installed Length, 3/4" Flange Diameter | McMaster-Carr
3D Printed Parts ESTIMATED PRICING USING 1KG ROLL COST: |  | $25.00
ID | Part | Material | QTY | Mass (g) / Unit | Time / Unit |  | Print Time (Min) | Estimated Price |  | Link
 | 65_Mounting_Plate_7.stl | PLA | 1 | 19 | 128 |  | $128.00 | $0.47
 | Hardware_Cover.stl | PLA | 1 | 1 | 10 |  | 10 | $0.03
 | Assembly_Washer.stl | PLA | 1 | 1 | 5 |  | 5 | $0.03
Custom Printed Circuit Board (PCB)
ID | Part |  | QTY
Tools for Assembly
 | Pliers
 | Small Screw Driver
 | 1/4"-20 UNC Bolt (Optional)
Alternatives (if there are other sources for some parts link them below)
ID | Part and description |  |  |  |  |  |  |  |  | Link
 | 5/16" x 1/4"-20 UNC Tee Nut Insert |  | 1 | 100 | $15.43 | 1 | $0.15 |  |  | Steel Tee Nut Inserts, 1/4"-20 Size, 0.36" Installed Length, 3/4" Flange Diameter | McMaster-Carr (https://www.mcmaster.com/90975A307/)
 | 7/16" x 1/4"-20 UNC Tee Nut Insert |  | 1 | 100 | $14.40 | 1 | $0.14 |  |  | Steel Tee Nut Inserts, 1/4"-20 Size, 0.485" Installed Length, 3/4" Flange Diameter | McMaster-Carr (https://www.mcmaster.com/90975A309/)
 | 9/16" x 1/4"-20 UNC Tee Nut Insert |  | 1 | 50 | $8.17 | 1 | $0.16 |  |  | Steel Tee Nut Inserts, 1/4"-20 Size, 0.61" Installed Length, 3/4" Flange Diameter | McMaster-Carr (https://www.mcmaster.com/90975A311/)

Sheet: BOM_M_9-16
Open Universal Mounting Plate - Medium Plate - 9/16 Tee Nut |  |  |  |  |  |  |  | Unit Cost | Total Cost | Total Print time (hr) | Total filament (g)
Version: V1.0 |  | Last Updated: 2023-Feb-27 |  |  |  |  |  | $0.74 | $8.74 | 2.45 | 23
Commercial Parts |  | Ensure to select the correct spreadsheet for your configoration
ID | Part Name | Part Type | QTY | QTY/PKG | $/PKG | PKG QTY | $/Unit | Extended | Total | Link
 | 9/16" x 1/4"-20 UNC Tee Nut | Fastener | 1 | 50 | $8.17 | 1 | $0.16 | $0.16 | $8.17 | Steel Tee Nut Inserts, 1/4"-20 Size, 0.61" Installed Length, 3/4" Flange Diameter | McMaster-Carr
3D Printed Parts ESTIMATED PRICING USING 1KG ROLL COST: |  | $25.00
ID | Part | Material | QTY | Mass (g) / Unit | Time / Unit |  | Print Time (Min) | Estimated Price |  | Link
 | 65_Mounting_Plate_9.stl | PLA | 1 | 21 | 137 |  | $137.00 | $0.53
 | Hardware_Cover.stl | PLA | 1 | 1 | 10 |  | 10 | $0.03
 | Assembly_Washer.stl | PLA | 1 | 1 | 5 |  | 5 | $0.03
Custom Printed Circuit Board (PCB)
ID | Part |  | QTY
Tools for Assembly
 | Pliers
 | Small Screw Driver
 | 1/4"-20 UNC Bolt (Optional)
Alternatives (if there are other sources for some parts link them below)
ID | Part and description |  |  |  |  |  |  |  |  | Link
 | 5/16" x 1/4"-20 UNC Tee Nut Insert |  | 1 | 100 | $15.43 | 1 | $0.15 |  |  | Steel Tee Nut Inserts, 1/4"-20 Size, 0.36" Installed Length, 3/4" Flange Diameter | McMaster-Carr (https://www.mcmaster.com/90975A307/)
 | 7/16" x 1/4"-20 UNC Tee Nut Insert |  | 1 | 100 | $14.40 | 1 | $0.14 |  |  | Steel Tee Nut Inserts, 1/4"-20 Size, 0.485" Installed Length, 3/4" Flange Diameter | McMaster-Carr (https://www.mcmaster.com/90975A309/)
 | 9/16" x 1/4"-20 UNC Tee Nut Insert |  | 1 | 50 | $8.17 | 1 | $0.16 |  |  | Steel Tee Nut Inserts, 1/4"-20 Size, 0.61" Installed Length, 3/4" Flange Diameter | McMaster-Carr (https://www.mcmaster.com/90975A311/)

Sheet: BOM_L_5-16
Open Universal Mounting Plate - Large Plate - 5/16 Tee Nut |  |  |  |  |  |  |  | Unit Cost | Total Cost | Total Print time (hr) | Total filament (g)
Version: V1.0 |  | Last Updated: 2023-Feb-27 |  |  |  |  |  | $3.51 | $3.52 | 3.48 | 29
Commercial Parts |  | Ensure to select the correct spreadsheet for your configoration
ID | Part Name | Part Type | QTY | QTY/PKG | $/PKG | PKG QTY | $/Unit | Extended | Total | Link
 | 5/16" x 1/4"-20 UNC Tee Nut | Fastener | 1 | 1 | $2.79 | 1 | $2.79 | $2.79 | $2.79 | Hillman Tee Nuts, Zinc | Canadian Tire
3D Printed Parts ESTIMATED PRICING USING 1KG ROLL COST: |  | $25.00
ID | Part | Material | QTY | Mass (g) / Unit | Time / Unit |  | Print Time (Min) | Estimated Price |  | Link
 | 85_Mounting_Plate_5.stl | PLA | 1 | 27 | 199 |  | $199.00 | $0.68
 | Hardware_Cover.stl | PLA | 1 | 1 | 10 |  | 10 | $0.03
 | Assembly_Washer.stl | PLA | 1 | 1 | 5 |  | 5 | $0.03
Custom Printed Circuit Board (PCB)
ID | Part |  | QTY
Tools for Assembly
 | Pliers
 | Small Screw Driver
 | 1/4"-20 UNC Bolt (Optional)
Alternatives (if there are other sources for some parts link them below)
ID | Part and description |  |  |  |  |  |  |  |  | Link
 | 5/16" x 1/4"-20 UNC Tee Nut Insert |  | 1 | 100 | $15.43 | 1 | $0.15 |  |  | Steel Tee Nut Inserts, 1/4"-20 Size, 0.36" Installed Length, 3/4" Flange Diameter | McMaster-Carr (https://www.mcmaster.com/90975A307/)
 | 7/16" x 1/4"-20 UNC Tee Nut Insert |  | 1 | 100 | $14.40 | 1 | $0.14 |  |  | Steel Tee Nut Inserts, 1/4"-20 Size, 0.485" Installed Length, 3/4" Flange Diameter | McMaster-Carr (https://www.mcmaster.com/90975A309/)
 | 9/16" x 1/4"-20 UNC Tee Nut Insert |  | 1 | 50 | $8.17 | 1 | $0.16 |  |  | Steel Tee Nut Inserts, 1/4"-20 Size, 0.61" Installed Length, 3/4" Flange Diameter | McMaster-Carr (https://www.mcmaster.com/90975A311/)

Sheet: BOM_L_7-16
Open Universal Mounting Plate - Large Plate - 7/16 Tee Nut |  |  |  |  |  |  |  | Unit Cost | Total Cost | Total Print time (hr) | Total filament (g)
Version: V1.0 |  | Last Updated: 2023-Feb-27 |  |  |  |  |  | $0.94 | $15.20 | 3.78 | 32
Commercial Parts |  | Ensure to select the correct spreadsheet for your configoration
ID | Part Name | Part Type | QTY | QTY/PKG | $/PKG | PKG QTY | $/Unit | Extended | Total | Link
 | 7/16" x 1/4"-20 UNC Tee Nut | Fastener | 1 | 100 | $14.40 | 1 | $0.14 | $0.14 | $14.40 | Steel Tee Nut Inserts, 1/4"-20 Size, 0.485" Installed Length, 3/4" Flange Diameter | McMaster-Carr
3D Printed Parts ESTIMATED PRICING USING 1KG ROLL COST: |  | $25.00
ID | Part | Material | QTY | Mass (g) / Unit | Time / Unit |  | Print Time (Min) | Estimated Price |  | Link
 | 85_Mounting_Plate_7.stl | PLA | 1 | 30 | 217 |  | $217.00 | $0.75
 | Hardware_Cover.stl | PLA | 1 | 1 | 10 |  | 10 | $0.03
 | Assembly_Washer.stl | PLA | 1 | 1 | 5 |  | 5 | $0.03
Custom Printed Circuit Board (PCB)
ID | Part |  | QTY
Tools for Assembly
 | Pliers
 | Small Screw Driver
 | 1/4"-20 UNC Bolt (Optional)
Alternatives (if there are other sources for some parts link them below)
ID | Part and description |  |  |  |  |  |  |  |  | Link
 | 5/16" x 1/4"-20 UNC Tee Nut Insert |  | 1 | 100 | $15.43 | 1 | $0.15 |  |  | Steel Tee Nut Inserts, 1/4"-20 Size, 0.36" Installed Length, 3/4" Flange Diameter | McMaster-Carr (https://www.mcmaster.com/90975A307/)
 | 7/16" x 1/4"-20 UNC Tee Nut Insert |  | 1 | 100 | $14.40 | 1 | $0.14 |  |  | Steel Tee Nut Inserts, 1/4"-20 Size, 0.485" Installed Length, 3/4" Flange Diameter | McMaster-Carr (https://www.mcmaster.com/90975A309/)
 | 9/16" x 1/4"-20 UNC Tee Nut Insert |  | 1 | 50 | $8.17 | 1 | $0.16 |  |  | Steel Tee Nut Inserts, 1/4"-20 Size, 0.61" Installed Length, 3/4" Flange Diameter | McMaster-Carr (https://www.mcmaster.com/90975A311/)

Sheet: BOM_L_9-16
Open Universal Mounting Plate - Large Plate - 9/16 Tee Nut |  |  |  |  |  |  |  | Unit Cost | Total Cost | Total Print time (hr) | Total filament (g)
Version: V1.0 |  | Last Updated: 2023-Feb-27 |  |  |  |  |  | $1.04 | $9.04 | 4.12 | 35
Commercial Parts |  | Ensure to select the correct spreadsheet for your configoration
ID | Part Name | Part Type | QTY | QTY/PKG | $/PKG | PKG QTY | $/Unit | Extended | Total | Link
 | 9/16" x 1/4"-20 UNC Tee Nut | Fastener | 1 | 50 | $8.17 | 1 | $0.16 | $0.16 | $8.17 | Steel Tee Nut Inserts, 1/4"-20 Size, 0.61" Installed Length, 3/4" Flange Diameter | McMaster-Carr
3D Printed Parts ESTIMATED PRICING USING 1KG ROLL COST: |  | $25.00
ID | Part | Material | QTY | Mass (g) / Unit | Time / Unit |  | Print Time (Min) | Estimated Price |  | Link
 | 85_Mounting_Plate_9.stl | PLA | 1 | 33 | 237 |  | $237.00 | $0.83
 | Hardware_Cover.stl | PLA | 1 | 1 | 10 |  | 10 | $0.03
 | Assembly_Washer.stl | PLA | 1 | 1 | 5 |  | 5 | $0.03
Custom Printed Circuit Board (PCB)
ID | Part |  | QTY
Tools for Assembly
 | Pliers
 | Small Screw Driver
 | 1/4"-20 UNC Bolt (Optional)
Alternatives (if there are other sources for some parts link them below)
ID | Part and description |  |  |  |  |  |  |  |  | Link
 | 5/16" x 1/4"-20 UNC Tee Nut Insert |  | 1 | 100 | $15.43 | 1 | $0.15 |  |  | Steel Tee Nut Inserts, 1/4"-20 Size, 0.36" Installed Length, 3/4" Flange Diameter | McMaster-Carr (https://www.mcmaster.com/90975A307/)
 | 7/16" x 1/4"-20 UNC Tee Nut Insert |  | 1 | 100 | $14.40 | 1 | $0.14 |  |  | Steel Tee Nut Inserts, 1/4"-20 Size, 0.485" Installed Length, 3/4" Flange Diameter | McMaster-Carr (https://www.mcmaster.com/90975A309/)
 | 9/16" x 1/4"-20 UNC Tee Nut Insert |  | 1 | 50 | $8.17 | 1 | $0.16 |  |  | Steel Tee Nut Inserts, 1/4"-20 Size, 0.61" Installed Length, 3/4" Flange Diameter | McMaster-Carr (https://www.mcmaster.com/90975A311/)

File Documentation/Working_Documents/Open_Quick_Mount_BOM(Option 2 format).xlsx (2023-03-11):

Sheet: BOM_S_5-16
<Device Name> |  | Small Plate - 5/16 Tee Nut |  |  |  |  |  | Unit Cost | Total Cost | Total Print time (hr) | Total filament (g)
Version: V1.0 |  | Last Updated: 2023-Feb-27 |  |  |  |  |  | $3.06 | $3.06 | 1.32 | 11
Commercial Parts
ID | Part Name | Part Type | QTY | QTY/PKG | $/PKG | PKG QTY | $/Unit | Extended | Total | Link
 | 5/16" x 1/4"-20 UNC Tee Nut | Fastener | 1 | 1 | $2.79 | 1 | $2.79 | $2.79 | $2.79 | Hillman Tee Nuts, Zinc | Canadian Tire
3D Printed Parts ESTIMATED PRICING USING 1KG ROLL COST: |  | $25.00
ID | Part | Material | QTY | Mass (g) / Unit | Time / Unit |  | Print Time (Min) | Estimated Price |  | Link
 | 45_Mounting_Plate_5.stl | PLA | 1 | 9 | 69 |  | $69.00 | $0.22 |  |  |  | 1
 | Hardware_Cover.stl | PLA | 1 | 1 | 10 |  | 10 | $0.03
 | Assembly_Washer.stl | PLA | 1 | 1 | 5 |  | 5 | $0.03 |  |  |  | 9
Custom Printed Circuit Board (PCB)
ID | Part |  | QTY
Tools for Assembly
 | Pliers
 | Small Screw Driver
 | 1/4"-20 UNC Bolt (Optional)
Alternatives (if there are other sources for some parts link them below)
ID | Part and description |  |  |  |  |  |  |  |  | Link
 | 5/16" x 1/4"-20 UNC Tee Nut Insert |  | 1 | 100 | $15.43 | 1 | $0.15 |  |  | Steel Tee Nut Inserts, 1/4"-20 Size, 0.36" Installed Length, 3/4" Flange Diameter | McMaster-Carr (https://www.mcmaster.com/90975A307/)
 | 7/16" x 1/4"-20 UNC Tee Nut Insert |  | 1 | 100 | $14.40 | 1 | $0.14 |  |  | Steel Tee Nut Inserts, 1/4"-20 Size, 0.485" Installed Length, 3/4" Flange Diameter | McMaster-Carr (https://www.mcmaster.com/90975A309/)
 | 9/16" x 1/4"-20 UNC Tee Nut Insert |  | 1 | 50 | $8.17 | 1 | $0.16 |  |  | Steel Tee Nut Inserts, 1/4"-20 Size, 0.61" Installed Length, 3/4" Flange Diameter | McMaster-Carr (https://www.mcmaster.com/90975A311/)

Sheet: BOM_S_7-16
<Device Name> |  | Small Plate - 7/16 Tee Nut |  |  |  |  |  | Unit Cost | Total Cost | Total Print time (hr) | Total filament (g)
Version: V1.0 |  | Last Updated: 2023-Feb-27 |  |  |  |  |  | $0.44 | $14.70 | 1.38 | 12
Commercial Parts
ID | Part Name | Part Type | QTY | QTY/PKG | $/PKG | PKG QTY | $/Unit | Extended | Total | Link
 | 7/16" x 1/4"-20 UNC Tee Nut | Fastener | 1 | 100 | $14.40 | 1 | $0.14 | $0.14 | $14.40 | Steel Tee Nut Inserts, 1/4"-20 Size, 0.485" Installed Length, 3/4" Flange Diameter | McMaster-Carr
3D Printed Parts ESTIMATED PRICING USING 1KG ROLL COST: |  | $25.00
ID | Part | Material | QTY | Mass (g) / Unit | Time / Unit |  | Print Time (Min) | Estimated Price |  | Link
 | 45_Mounting_Plate_7.stl | PLA | 1 | 10 | 73 |  | $73.00 | $0.25 |  |  |  | 1
 | Hardware_Cover.stl | PLA | 1 | 1 | 10 |  | 10 | $0.03
 | Assembly_Washer.stl | PLA | 1 | 1 | 5 |  | 5 | $0.03 |  |  |  | 13
Custom Printed Circuit Board (PCB)
ID | Part |  | QTY
Tools for Assembly
 | Pliers
 | Small Screw Driver
 | 1/4"-20 UNC Bolt (Optional)
Alternatives (if there are other sources for some parts link them below)
ID | Part and description |  |  |  |  |  |  |  |  | Link
 | 5/16" x 1/4"-20 UNC Tee Nut Insert |  | 1 | 100 | $15.43 | 1 | $0.15 |  |  | Steel Tee Nut Inserts, 1/4"-20 Size, 0.36" Installed Length, 3/4" Flange Diameter | McMaster-Carr (https://www.mcmaster.com/90975A307/)
 | 7/16" x 1/4"-20 UNC Tee Nut Insert |  | 1 | 100 | $14.40 | 1 | $0.14 |  |  | Steel Tee Nut Inserts, 1/4"-20 Size, 0.485" Installed Length, 3/4" Flange Diameter | McMaster-Carr (https://www.mcmaster.com/90975A309/)
 | 9/16" x 1/4"-20 UNC Tee Nut Insert |  | 1 | 50 | $8.17 | 1 | $0.16 |  |  | Steel Tee Nut Inserts, 1/4"-20 Size, 0.61" Installed Length, 3/4" Flange Diameter | McMaster-Carr (https://www.mcmaster.com/90975A311/)

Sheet: BOM_S_9-16
<Device Name> |  | Small Plate - 9/16 Tee Nut |  |  |  |  |  | Unit Cost | Total Cost | Total Print time (hr) | Total filament (g)
Version: V1.0 |  | Last Updated: 2023-Feb-27 |  |  |  |  |  | $0.49 | $8.49 | 1.48 | 13
Commercial Parts
ID | Part Name | Part Type | QTY | QTY/PKG | $/PKG | PKG QTY | $/Unit | Extended | Total | Link
 | 9/16" x 1/4"-20 UNC Tee Nut | Fastener | 1 | 50 | $8.17 | 1 | $0.16 | $0.16 | $8.17 | Steel Tee Nut Inserts, 1/4"-20 Size, 0.61" Installed Length, 3/4" Flange Diameter | McMaster-Carr
3D Printed Parts ESTIMATED PRICING USING 1KG ROLL COST: |  | $25.00
ID | Part | Material | QTY | Mass (g) / Unit | Time / Unit |  | Print Time (Min) | Estimated Price |  | Link
 | 45_Mounting_Plate_9.stl | PLA | 1 | 11 | 79 |  | $79.00 | $0.27 |  |  |  | 1
 | Hardware_Cover.stl | PLA | 1 | 1 | 10 |  | 10 | $0.03
 | Assembly_Washer.stl | PLA | 1 | 1 | 5 |  | 5 | $0.03 |  |  |  | 19
Custom Printed Circuit Board (PCB)
ID | Part |  | QTY
Tools for Assembly
 | Pliers
 | Small Screw Driver
 | 1/4"-20 UNC Bolt (Optional)
Alternatives (if there are other sources for some parts link them below)
ID | Part and description |  |  |  |  |  |  |  |  | Link
 | 5/16" x 1/4"-20 UNC Tee Nut Insert |  | 1 | 100 | $15.43 | 1 | $0.15 |  |  | Steel Tee Nut Inserts, 1/4"-20 Size, 0.36" Installed Length, 3/4" Flange Diameter | McMaster-Carr (https://www.mcmaster.com/90975A307/)
 | 7/16" x 1/4"-20 UNC Tee Nut Insert |  | 1 | 100 | $14.40 | 1 | $0.14 |  |  | Steel Tee Nut Inserts, 1/4"-20 Size, 0.485" Installed Length, 3/4" Flange Diameter | McMaster-Carr (https://www.mcmaster.com/90975A309/)
 | 9/16" x 1/4"-20 UNC Tee Nut Insert |  | 1 | 50 | $8.17 | 1 | $0.16 |  |  | Steel Tee Nut Inserts, 1/4"-20 Size, 0.61" Installed Length, 3/4" Flange Diameter | McMaster-Carr (https://www.mcmaster.com/90975A311/)

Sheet: BOM_M_5-16
<Device Name> |  | Medium Plate - 5/16 Tee Nut |  |  |  |  |  | Unit Cost | Total Cost | Total Print time (hr) | Total filament (g)
Version: V1.0 |  | Last Updated: 2023-Feb-27 |  |  |  |  |  | $3.26 | $3.27 | 2.40 | 19
Commercial Parts
ID | Part Name | Part Type | QTY | QTY/PKG | $/PKG | PKG QTY | $/Unit | Extended | Total | Link
 | 5/16" x 1/4"-20 UNC Tee Nut | Fastener | 1 | 1 | $2.79 | 1 | $2.79 | $2.79 | $2.79 | Hillman Tee Nuts, Zinc | Canadian Tire
3D Printed Parts ESTIMATED PRICING USING 1KG ROLL COST: |  | $25.00
ID | Part | Material | QTY | Mass (g) / Unit | Time / Unit |  | Print Time (Min) | Estimated Price |  | Link
 | 65_Mounting_Plate_5.stl | PLA | 1 | 17 | 134 |  | $134.00 | $0.43 |  |  |  | 2
 | Hardware_Cover.stl | PLA | 1 | 1 | 10 |  | 10 | $0.03
 | Assembly_Washer.stl | PLA | 1 | 1 | 5 |  | 5 | $0.03 |  |  |  | 14
Custom Printed Circuit Board (PCB)
ID | Part |  | QTY
Tools for Assembly
 | Pliers
 | Small Screw Driver
 | 1/4"-20 UNC Bolt (Optional)
Alternatives (if there are other sources for some parts link them below)
ID | Part and description |  |  |  |  |  |  |  |  | Link
 | 5/16" x 1/4"-20 UNC Tee Nut Insert |  | 1 | 100 | $15.43 | 1 | $0.15 |  |  | Steel Tee Nut Inserts, 1/4"-20 Size, 0.36" Installed Length, 3/4" Flange Diameter | McMaster-Carr (https://www.mcmaster.com/90975A307/)
 | 7/16" x 1/4"-20 UNC Tee Nut Insert |  | 1 | 100 | $14.40 | 1 | $0.14 |  |  | Steel Tee Nut Inserts, 1/4"-20 Size, 0.485" Installed Length, 3/4" Flange Diameter | McMaster-Carr (https://www.mcmaster.com/90975A309/)
 | 9/16" x 1/4"-20 UNC Tee Nut Insert |  | 1 | 50 | $8.17 | 1 | $0.16 |  |  | Steel Tee Nut Inserts, 1/4"-20 Size, 0.61" Installed Length, 3/4" Flange Diameter | McMaster-Carr (https://www.mcmaster.com/90975A311/)

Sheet: BOM_M_7-16
<Device Name> |  | Medium Plate - 7/16 Tee Nut |  |  |  |  |  | Unit Cost | Total Cost | Total Print time (hr) | Total filament (g)
Version: V1.0 |  | Last Updated: 2023-Feb-27 |  |  |  |  |  | $0.67 | $14.93 | 2.30 | 21
Commercial Parts
ID | Part Name | Part Type | QTY | QTY/PKG | $/PKG | PKG QTY | $/Unit | Extended | Total | Link
 | 7/16" x 1/4"-20 UNC Tee Nut | Fastener | 1 | 100 | $14.40 | 1 | $0.14 | $0.14 | $14.40 | Steel Tee Nut Inserts, 1/4"-20 Size, 0.485" Installed Length, 3/4" Flange Diameter | McMaster-Carr
3D Printed Parts ESTIMATED PRICING USING 1KG ROLL COST: |  | $25.00
ID | Part | Material | QTY | Mass (g) / Unit | Time / Unit |  | Print Time (Min) | Estimated Price |  | Link
 | 65_Mounting_Plate_7.stl | PLA | 1 | 19 | 128 |  | $128.00 | $0.47 |  |  |  | 2
 | Hardware_Cover.stl | PLA | 1 | 1 | 10 |  | 10 | $0.03
 | Assembly_Washer.stl | PLA | 1 | 1 | 5 |  | 5 | $0.03 |  |  |  | 8
Custom Printed Circuit Board (PCB)
ID | Part |  | QTY
Tools for Assembly
 | Pliers
 | Small Screw Driver
 | 1/4"-20 UNC Bolt (Optional)
Alternatives (if there are other sources for some parts link them below)
ID | Part and description |  |  |  |  |  |  |  |  | Link
 | 5/16" x 1/4"-20 UNC Tee Nut Insert |  | 1 | 100 | $15.43 | 1 | $0.15 |  |  | Steel Tee Nut Inserts, 1/4"-20 Size, 0.36" Installed Length, 3/4" Flange Diameter | McMaster-Carr (https://www.mcmaster.com/90975A307/)
 | 7/16" x 1/4"-20 UNC Tee Nut Insert |  | 1 | 100 | $14.40 | 1 | $0.14 |  |  | Steel Tee Nut Inserts, 1/4"-20 Size, 0.485" Installed Length, 3/4" Flange Diameter | McMaster-Carr (https://www.mcmaster.com/90975A309/)
 | 9/16" x 1/4"-20 UNC Tee Nut Insert |  | 1 | 50 | $8.17 | 1 | $0.16 |  |  | Steel Tee Nut Inserts, 1/4"-20 Size, 0.61" Installed Length, 3/4" Flange Diameter | McMaster-Carr (https://www.mcmaster.com/90975A311/)

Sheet: BOM_M_9-16
<Device Name> |  | Medium Plate - 9/16 Tee Nut |  |  |  |  |  | Unit Cost | Total Cost | Total Print time (hr) | Total filament (g)
Version: V1.0 |  | Last Updated: 2023-Feb-27 |  |  |  |  |  | $0.74 | $8.74 | 2.45 | 23
Commercial Parts
ID | Part Name | Part Type | QTY | QTY/PKG | $/PKG | PKG QTY | $/Unit | Extended | Total | Link
 | 9/16" x 1/4"-20 UNC Tee Nut | Fastener | 1 | 50 | $8.17 | 1 | $0.16 | $0.16 | $8.17 | Steel Tee Nut Inserts, 1/4"-20 Size, 0.61" Installed Length, 3/4" Flange Diameter | McMaster-Carr
3D Printed Parts ESTIMATED PRICING USING 1KG ROLL COST: |  | $25.00
ID | Part | Material | QTY | Mass (g) / Unit | Time / Unit |  | Print Time (Min) | Estimated Price |  | Link
 | 65_Mounting_Plate_9.stl | PLA | 1 | 21 | 137 |  | $137.00 | $0.53 |  |  |  | 2
 | Hardware_Cover.stl | PLA | 1 | 1 | 10 |  | 10 | $0.03
 | Assembly_Washer.stl | PLA | 1 | 1 | 5 |  | 5 | $0.03 |  |  |  | 17
Custom Printed Circuit Board (PCB)
ID | Part |  | QTY
Tools for Assembly
 | Pliers
 | Small Screw Driver
 | 1/4"-20 UNC Bolt (Optional)
Alternatives (if there are other sources for some parts link them below)
ID | Part and description |  |  |  |  |  |  |  |  | Link
 | 5/16" x 1/4"-20 UNC Tee Nut Insert |  | 1 | 100 | $15.43 | 1 | $0.15 |  |  | Steel Tee Nut Inserts, 1/4"-20 Size, 0.36" Installed Length, 3/4" Flange Diameter | McMaster-Carr (https://www.mcmaster.com/90975A307/)
 | 7/16" x 1/4"-20 UNC Tee Nut Insert |  | 1 | 100 | $14.40 | 1 | $0.14 |  |  | Steel Tee Nut Inserts, 1/4"-20 Size, 0.485" Installed Length, 3/4" Flange Diameter | McMaster-Carr (https://www.mcmaster.com/90975A309/)
 | 9/16" x 1/4"-20 UNC Tee Nut Insert |  | 1 | 50 | $8.17 | 1 | $0.16 |  |  | Steel Tee Nut Inserts, 1/4"-20 Size, 0.61" Installed Length, 3/4" Flange Diameter | McMaster-Carr (https://www.mcmaster.com/90975A311/)

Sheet: BOM_L_5-16
<Device Name> |  | Large Plate - 5/16 Tee Nut |  |  |  |  |  | Unit Cost | Total Cost | Total Print time (hr) | Total filament (g)
Version: V1.0 |  | Last Updated: 2023-Feb-27 |  |  |  |  |  | $3.51 | $3.52 | 3.48 | 29
Commercial Parts
ID | Part Name | Part Type | QTY | QTY/PKG | $/PKG | PKG QTY | $/Unit | Extended | Total | Link
 | 5/16" x 1/4"-20 UNC Tee Nut | Fastener | 1 | 1 | $2.79 | 1 | $2.79 | $2.79 | $2.79 | Hillman Tee Nuts, Zinc | Canadian Tire
3D Printed Parts ESTIMATED PRICING USING 1KG ROLL COST: |  | $25.00
ID | Part | Material | QTY | Mass (g) / Unit | Time / Unit |  | Print Time (Min) | Estimated Price |  | Link
 | 85_Mounting_Plate_5.stl | PLA | 1 | 27 | 199 |  | $199.00 | $0.68 |  |  |  | 3
 | Hardware_Cover.stl | PLA | 1 | 1 | 10 |  | 10 | $0.03
 | Assembly_Washer.stl | PLA | 1 | 1 | 5 |  | 5 | $0.03 |  |  |  | 19
Custom Printed Circuit Board (PCB)
ID | Part |  | QTY
Tools for Assembly
 | Pliers
 | Small Screw Driver
 | 1/4"-20 UNC Bolt (Optional)
Alternatives (if there are other sources for some parts link them below)
ID | Part and description |  |  |  |  |  |  |  |  | Link
 | 5/16" x 1/4"-20 UNC Tee Nut Insert |  | 1 | 100 | $15.43 | 1 | $0.15 |  |  | Steel Tee Nut Inserts, 1/4"-20 Size, 0.36" Installed Length, 3/4" Flange Diameter | McMaster-Carr (https://www.mcmaster.com/90975A307/)
 | 7/16" x 1/4"-20 UNC Tee Nut Insert |  | 1 | 100 | $14.40 | 1 | $0.14 |  |  | Steel Tee Nut Inserts, 1/4"-20 Size, 0.485" Installed Length, 3/4" Flange Diameter | McMaster-Carr (https://www.mcmaster.com/90975A309/)
 | 9/16" x 1/4"-20 UNC Tee Nut Insert |  | 1 | 50 | $8.17 | 1 | $0.16 |  |  | Steel Tee Nut Inserts, 1/4"-20 Size, 0.61" Installed Length, 3/4" Flange Diameter | McMaster-Carr (https://www.mcmaster.com/90975A311/)

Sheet: BOM_L_7-16
<Device Name> |  | Large Plate - 7/16 Tee Nut |  |  |  |  |  | Unit Cost | Total Cost | Total Print time (hr) | Total filament (g)
Version: V1.0 |  | Last Updated: 2023-Feb-27 |  |  |  |  |  | $0.94 | $15.20 | 3.78 | 32
Commercial Parts
ID | Part Name | Part Type | QTY | QTY/PKG | $/PKG | PKG QTY | $/Unit | Extended | Total | Link
 | 7/16" x 1/4"-20 UNC Tee Nut | Fastener | 1 | 100 | $14.40 | 1 | $0.14 | $0.14 | $14.40 | Steel Tee Nut Inserts, 1/4"-20 Size, 0.485" Installed Length, 3/4" Flange Diameter | McMaster-Carr
3D Printed Parts ESTIMATED PRICING USING 1KG ROLL COST: |  | $25.00
ID | Part | Material | QTY | Mass (g) / Unit | Time / Unit |  | Print Time (Min) | Estimated Price |  | Link
 | 85_Mounting_Plate_7.stl | PLA | 1 | 30 | 217 |  | $217.00 | $0.75 |  |  |  | 3
 | Hardware_Cover.stl | PLA | 1 | 1 | 10 |  | 10 | $0.03
 | Assembly_Washer.stl | PLA | 1 | 1 | 5 |  | 5 | $0.03 |  |  |  | 37
Custom Printed Circuit Board (PCB)
ID | Part |  | QTY
Tools for Assembly
 | Pliers
 | Small Screw Driver
 | 1/4"-20 UNC Bolt (Optional)
Alternatives (if there are other sources for some parts link them below)
ID | Part and description |  |  |  |  |  |  |  |  | Link
 | 5/16" x 1/4"-20 UNC Tee Nut Insert |  | 1 | 100 | $15.43 | 1 | $0.15 |  |  | Steel Tee Nut Inserts, 1/4"-20 Size, 0.36" Installed Length, 3/4" Flange Diameter | McMaster-Carr (https://www.mcmaster.com/90975A307/)
 | 7/16" x 1/4"-20 UNC Tee Nut Insert |  | 1 | 100 | $14.40 | 1 | $0.14 |  |  | Steel Tee Nut Inserts, 1/4"-20 Size, 0.485" Installed Length, 3/4" Flange Diameter | McMaster-Carr (https://www.mcmaster.com/90975A309/)
 | 9/16" x 1/4"-20 UNC Tee Nut Insert |  | 1 | 50 | $8.17 | 1 | $0.16 |  |  | Steel Tee Nut Inserts, 1/4"-20 Size, 0.61" Installed Length, 3/4" Flange Diameter | McMaster-Carr (https://www.mcmaster.com/90975A311/)

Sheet: BOM_L_9-16
<Device Name> |  | Large Plate - 9/16 Tee Nut |  |  |  |  |  | Unit Cost | Total Cost | Total Print time (hr) | Total filament (g)
Version: V1.0 |  | Last Updated: 2023-Feb-27 |  |  |  |  |  | $1.04 | $9.04 | 4.12 | 35
Commercial Parts
ID | Part Name | Part Type | QTY | QTY/PKG | $/PKG | PKG QTY | $/Unit | Extended | Total | Link
 | 9/16" x 1/4"-20 UNC Tee Nut | Fastener | 1 | 50 | $8.17 | 1 | $0.16 | $0.16 | $8.17 | Steel Tee Nut Inserts, 1/4"-20 Size, 0.61" Installed Length, 3/4" Flange Diameter | McMaster-Carr
3D Printed Parts ESTIMATED PRICING USING 1KG ROLL COST: |  | $25.00
ID | Part | Material | QTY | Mass (g) / Unit | Time / Unit |  | Print Time (Min) | Estimated Price |  | Link
 | 85_Mounting_Plate_9.stl | PLA | 1 | 33 | 237 |  | $237.00 | $0.83 |  |  |  | 3
 | Hardware_Cover.stl | PLA | 1 | 1 | 10 |  | 10 | $0.03
 | Assembly_Washer.stl | PLA | 1 | 1 | 5 |  | 5 | $0.03 |  |  |  | 57
Custom Printed Circuit Board (PCB)
ID | Part |  | QTY
Tools for Assembly
 | Pliers
 | Small Screw Driver
 | 1/4"-20 UNC Bolt (Optional)
Alternatives (if there are other sources for some parts link them below)
ID | Part and description |  |  |  |  |  |  |  |  | Link
 | 5/16" x 1/4"-20 UNC Tee Nut Insert |  | 1 | 100 | $15.43 | 1 | $0.15 |  |  | Steel Tee Nut Inserts, 1/4"-20 Size, 0.36" Installed Length, 3/4" Flange Diameter | McMaster-Carr (https://www.mcmaster.com/90975A307/)
 | 7/16" x 1/4"-20 UNC Tee Nut Insert |  | 1 | 100 | $14.40 | 1 | $0.14 |  |  | Steel Tee Nut Inserts, 1/4"-20 Size, 0.485" Installed Length, 3/4" Flange Diameter | McMaster-Carr (https://www.mcmaster.com/90975A309/)
 | 9/16" x 1/4"-20 UNC Tee Nut Insert |  | 1 | 50 | $8.17 | 1 | $0.16 |  |  | Steel Tee Nut Inserts, 1/4"-20 Size, 0.61" Installed Length, 3/4" Flange Diameter | McMaster-Carr (https://www.mcmaster.com/90975A311/)

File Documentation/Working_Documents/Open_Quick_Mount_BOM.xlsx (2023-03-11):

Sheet: BOM
Name TBD |  | Mounting Plate Selection: Use Drop Down List |  | Last Updated: 2023-Feb-27 |  |  |  | Unit Cost | Total Cost | Total Print time (hr) | Total filament (g)
Version: V1.0 |  | Medium Plate - 7/16 Tee Nut |  |  |  |  |  | $0.67 | $14.93 | 2.30 | 21
Commercial Parts |  | Note: Please select the correct device selection above to get accurate part and cost estimations.
ID | Part Name | Part Type | QTY | QTY/PKG | $/PKG | PKG QTY | $/Unit | Extended | Total | Link
 | 7/16" x 1/4"-20 UNC Tee Nut | Fastener | 1 | 100 | $14.40 | 1 | $0.14 | $0.14 | $14.40 | Steel Tee Nut Inserts, 1/4"-20 Size, 0.485" Installed Length, 3/4" Flange Diameter | McMaster-Carr
3D Printed Parts ESTIMATED PRICING USING 1KG ROLL COST: |  | $25.00
ID | Part | Material | QTY | Mass (g) / Unit | Time / Unit |  | Print Time (Min) | Estimated Price
 | 65_Mounting_Plate_7.stl | PLA | 1 | 19 | 128 |  | 128 | $0.47 |  |  |  | 2
 | Hardware_Cover.stl | PLA | 1 | 1 | 10 |  | 10 | $0.03
 | Assembly_Washer.stl | PLA | 1 | 1 | 5 |  | 5 | $0.03 |  |  |  | 8
Custom Printed Circuit Board (PCB)
ID | Part |  | QTY
 | Not Required
Tools for Assembly
 | Pliers
 | Small Screw Driver
 | 1/4"-20 UNC Bolt (Optional)
Alternatives (if there are other sources for some parts link them below)
ID | Part and description |  | QTY | QTY/PKG | $/PKG | PKG QTY | $/Unit |  |  | Link
 | 5/16" x 1/4"-20 UNC Tee Nut Insert |  | 1 | 100 | $15.43 | 1 | $0.15 |  |  | Steel Tee Nut Inserts, 1/4"-20 Size, 0.36" Installed Length, 3/4" Flange Diameter | McMaster-Carr (https://www.mcmaster.com/90975A307/)
 | 7/16" x 1/4"-20 UNC Tee Nut Insert |  | 1 | 100 | $14.40 | 1 | $0.14 |  |  | Steel Tee Nut Inserts, 1/4"-20 Size, 0.485" Installed Length, 3/4" Flange Diameter | McMaster-Carr (https://www.mcmaster.com/90975A309/)
 | 9/16" x 1/4"-20 UNC Tee Nut Insert |  | 1 | 50 | $8.17 | 1 | $0.16 |  |  | Steel Tee Nut Inserts, 1/4"-20 Size, 0.61" Installed Length, 3/4" Flange Diameter | McMaster-Carr (https://www.mcmaster.com/90975A311/)

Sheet: Device Option Details
Mounting Plate Options | Tee Nut | QTY/PKG | $/PKG | PKG QTY | Time / Unit | Mass (g) / Unit | Print File | Hardware Link
Small Plate - 5/16 Tee Nut | 5/16" x 1/4"-20 UNC Tee Nut | 1 | $2.79 | 1 | 69 | 9 | 45_Mounting_Plate_5.stl | Hillman Tee Nuts, Zinc | Canadian Tire (https://www.canadiantire.ca/en/pdp/hillman-tee-nuts-zinc-1612084p.1612085.html?loc=plp)
Small Plate - 7/16 Tee Nut | 7/16" x 1/4"-20 UNC Tee Nut | 100 | $14.40 | 1 | 73 | 10 | 45_Mounting_Plate_7.stl | Steel Tee Nut Inserts, 1/4"-20 Size, 0.485" Installed Length, 3/4" Flange Diameter | McMaster-Carr (https://www.mcmaster.com/90975A309/)
Small Plate - 9/16 Tee Nut | 9/16" x 1/4"-20 UNC Tee Nut | 50 | $8.17 | 1 | 79 | 11 | 45_Mounting_Plate_9.stl | Steel Tee Nut Inserts, 1/4"-20 Size, 0.61" Installed Length, 3/4" Flange Diameter | McMaster-Carr (https://www.mcmaster.com/90975A311/)
Medium Plate - 5/16 Tee Nut | 5/16" x 1/4"-20 UNC Tee Nut | 1 | $2.79 | 1 | 134 | 17 | 65_Mounting_Plate_5.stl | Hillman Tee Nuts, Zinc | Canadian Tire (https://www.canadiantire.ca/en/pdp/hillman-tee-nuts-zinc-1612084p.1612085.html?loc=plp)
Medium Plate - 7/16 Tee Nut | 7/16" x 1/4"-20 UNC Tee Nut | 100 | $14.40 | 1 | 128 | 19 | 65_Mounting_Plate_7.stl | Steel Tee Nut Inserts, 1/4"-20 Size, 0.485" Installed Length, 3/4" Flange Diameter | McMaster-Carr (https://www.mcmaster.com/90975A309/)
Medium Plate - 9/16 Tee Nut | 9/16" x 1/4"-20 UNC Tee Nut | 50 | $8.17 | 1 | 137 | 21 | 65_Mounting_Plate_9.stl | Steel Tee Nut Inserts, 1/4"-20 Size, 0.61" Installed Length, 3/4" Flange Diameter | McMaster-Carr (https://www.mcmaster.com/90975A311/)
Large Plate - 5/16 Tee Nut | 5/16" x 1/4"-20 UNC Tee Nut | 1 | $2.79 | 1 | 199 | 27 | 85_Mounting_Plate_5.stl | Hillman Tee Nuts, Zinc | Canadian Tire (https://www.canadiantire.ca/en/pdp/hillman-tee-nuts-zinc-1612084p.1612085.html?loc=plp)
Large Plate - 7/16 Tee Nut | 7/16" x 1/4"-20 UNC Tee Nut | 100 | $14.40 | 1 | 217 | 30 | 85_Mounting_Plate_7.stl | Steel Tee Nut Inserts, 1/4"-20 Size, 0.485" Installed Length, 3/4" Flange Diameter | McMaster-Carr (https://www.mcmaster.com/90975A309/)
Large Plate - 9/16 Tee Nut | 9/16" x 1/4"-20 UNC Tee Nut | 50 | $8.17 | 1 | 237 | 33 | 85_Mounting_Plate_9.stl | Steel Tee Nut Inserts, 1/4"-20 Size, 0.61" Installed Length, 3/4" Flange Diameter | McMaster-Carr (https://www.mcmaster.com/90975A311/)

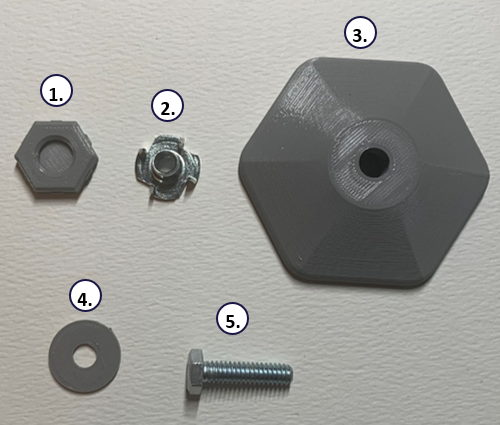
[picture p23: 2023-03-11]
Photos/Assembly_Photos/Labelled_Parts_List.png

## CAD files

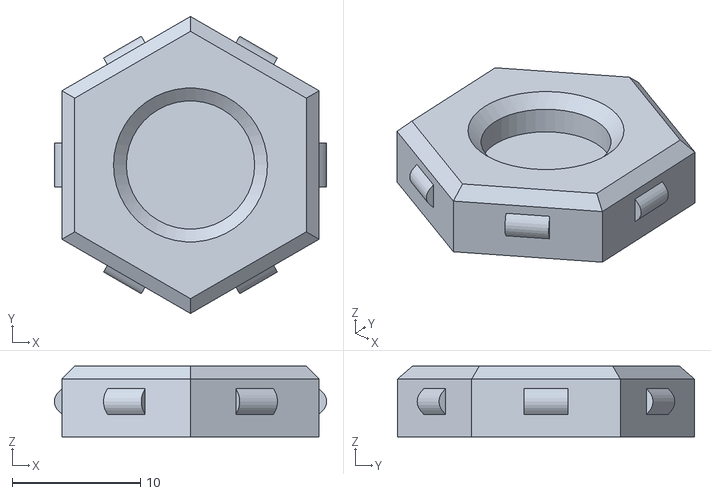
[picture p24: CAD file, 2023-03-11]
Build_Files/3D_Printing_Files/Hardware_Cover.stl
21.2 x 23.2 x 5.50

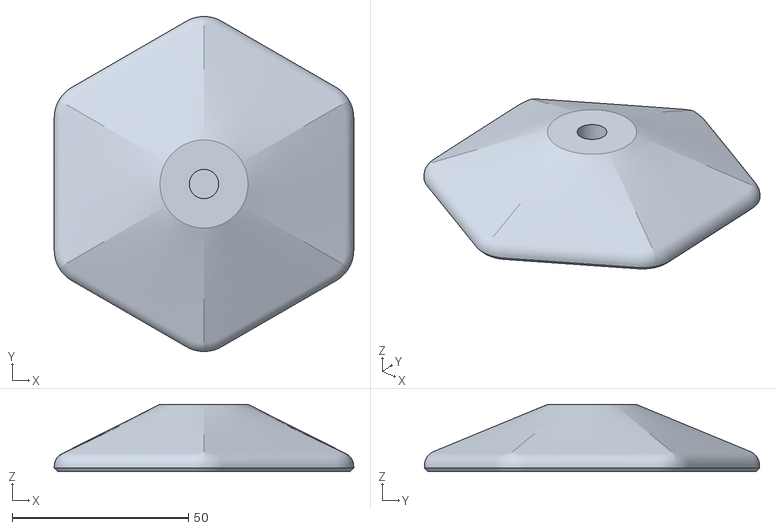
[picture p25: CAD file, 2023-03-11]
Build_Files/3D_Printing_Files/Large Mounting Plates/85_Mounting_Plate_7.stl
85.0 x 95.1 x 19.1

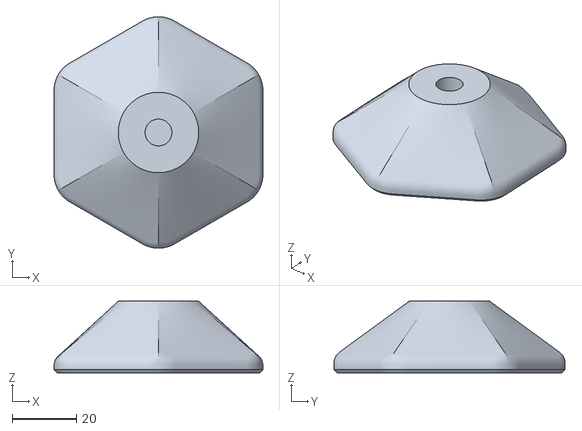
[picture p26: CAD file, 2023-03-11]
Build_Files/3D_Printing_Files/Medium Mounting Plates/65_Mounting_Plate_9.stl
65.0 x 72.0 x 22.3

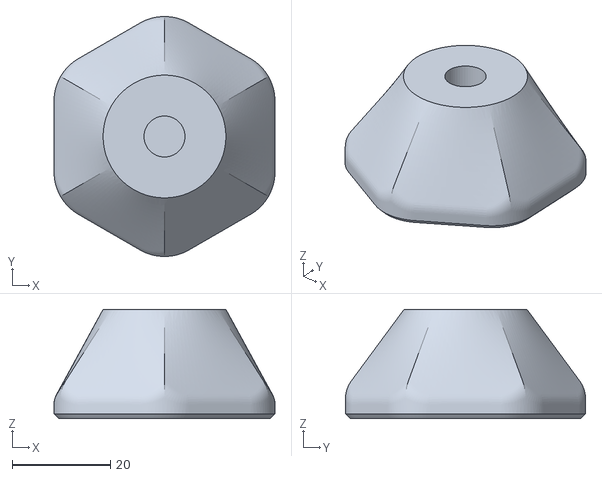
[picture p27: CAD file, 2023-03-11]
Build_Files/3D_Printing_Files/Small Mounting Plates/45_Mounting_Plate_9.stl
45.0 x 48.9 x 22.3

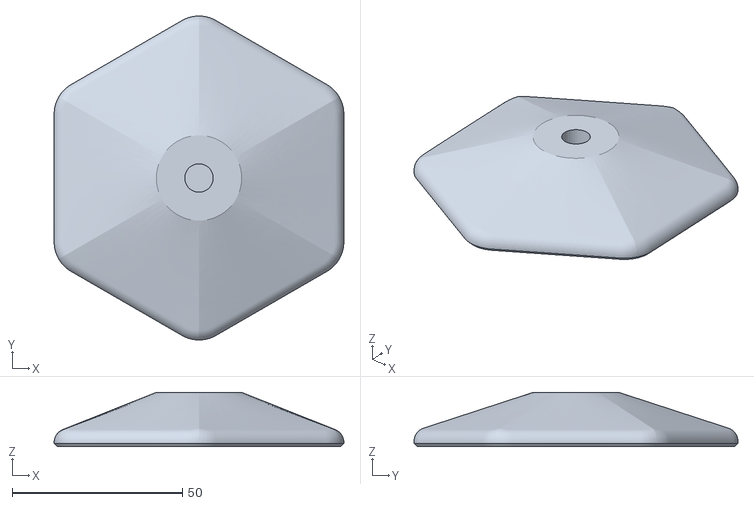
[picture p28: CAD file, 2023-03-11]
Build_Files/3D_Printing_Files/Large Mounting Plates/85_Mounting_Plate_5.stl
85.0 x 95.1 x 15.9

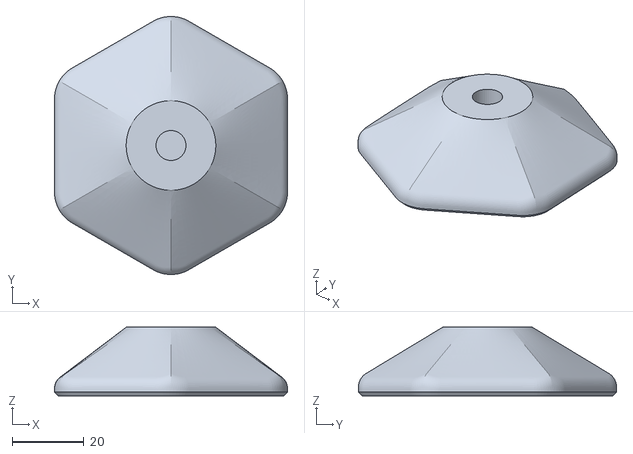
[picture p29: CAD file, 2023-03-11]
Build_Files/3D_Printing_Files/Medium Mounting Plates/65_Mounting_Plate_7.stl
65.0 x 72.0 x 19.1

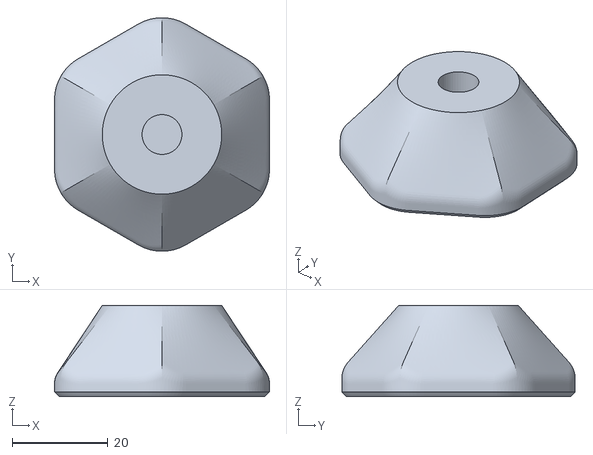
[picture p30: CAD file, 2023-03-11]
Build_Files/3D_Printing_Files/Small Mounting Plates/45_Mounting_Plate_7.stl
45.0 x 48.9 x 19.1

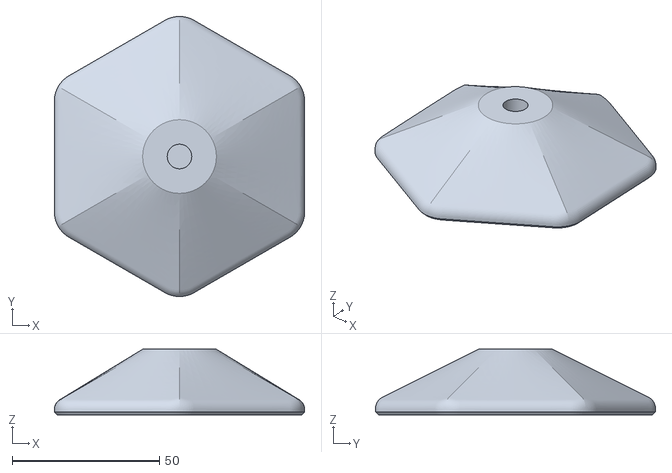
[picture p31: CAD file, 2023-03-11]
Build_Files/3D_Printing_Files/Large Mounting Plates/85_Mounting_Plate_9.stl
85.0 x 95.1 x 22.3

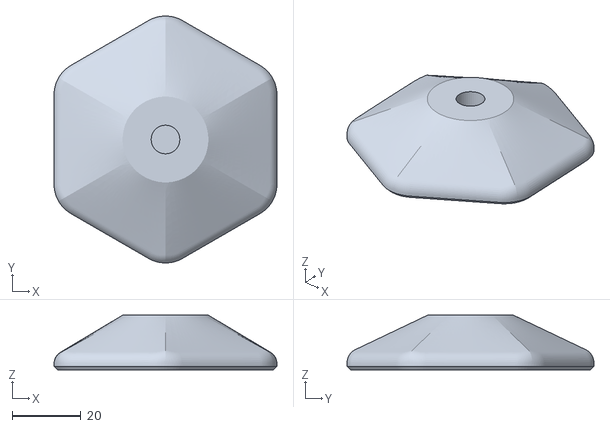
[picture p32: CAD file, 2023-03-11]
Build_Files/3D_Printing_Files/Medium Mounting Plates/65_Mounting_Plate_5.stl
65.0 x 72.0 x 15.9

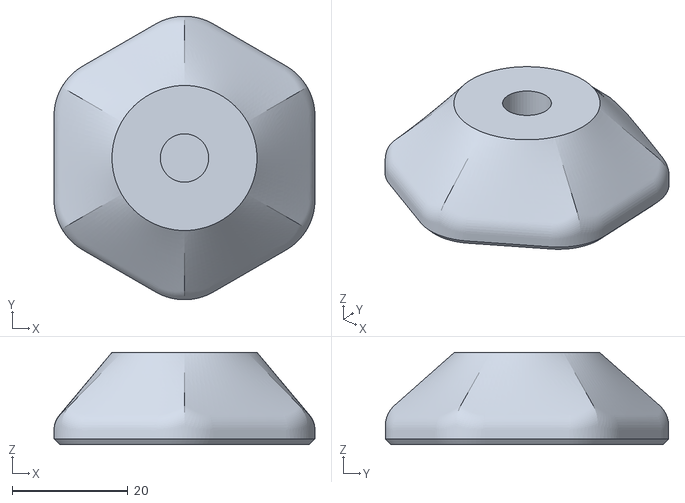
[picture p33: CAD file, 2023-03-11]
Build_Files/3D_Printing_Files/Small Mounting Plates/45_Mounting_Plate_5.stl
45.0 x 48.9 x 15.9

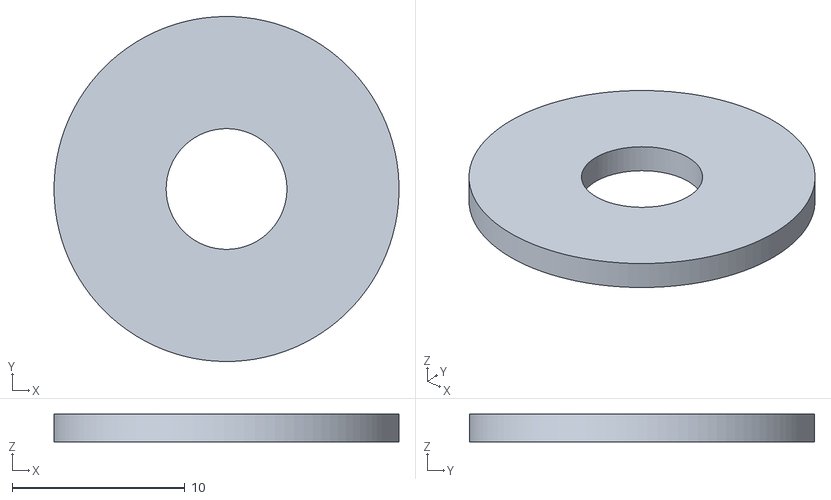
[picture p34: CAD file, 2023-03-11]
Build_Files/3D_Printing_Files/Assembly_Washer.stl
20.0 x 20.0 x 1.60

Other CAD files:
Design_Files/Mounting Plate Parametric .f3d

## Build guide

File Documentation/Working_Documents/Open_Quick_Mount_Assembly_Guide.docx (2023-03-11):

# Required Components

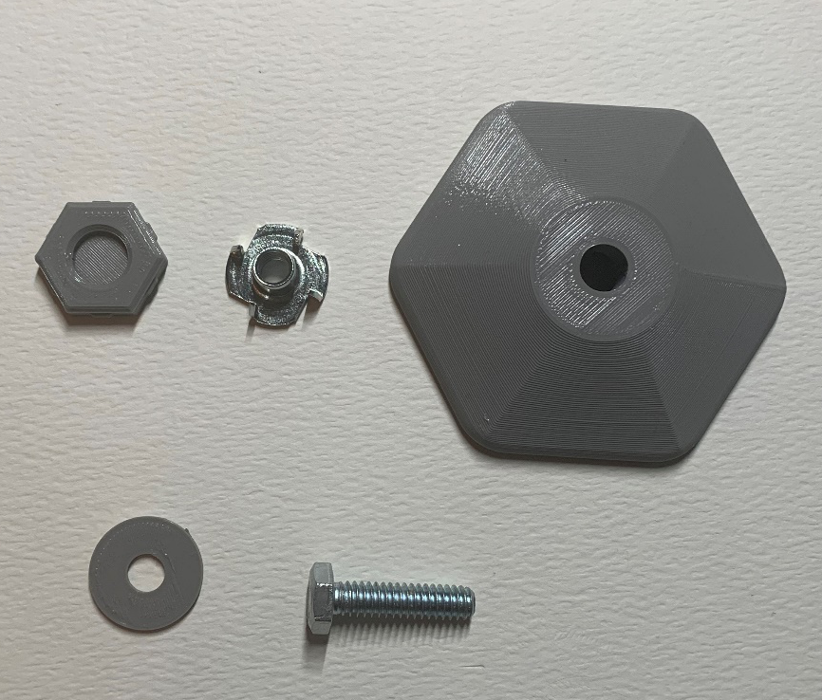
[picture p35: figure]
Five items for assembly: a 3D printed hardware cover, a tee nut insert, a 3D printed mounting plate, a 3D printed assembly washer, and a bolt.

5. 4. 3. 2. 1. | BOM 1. Hardware Cover 2. ¼”-20 UNC Tee Nut 3. Mounting Plate 4. Assembly Washer 5. ¼”-20 UNC Bolt (Optional)

# Required Tools

- Pliers
- Small Flat Head Screwdriver

# Required Personal Protective Equipment (PPE)

- Safety Glasses

# Mounting Plate Assembly Instructions

## Step 1: Align the Tee Nut

Align the prongs of the Tee Nut with their corresponding holes in the mounting plate. These holes may be covered by the sacrificial bridge used for printing, so a small flathead screwdriver can be used to pierce the mounting holes to make it easier to install.

Note: There are mounting holes for three-, four-, and six-pronged Tee Nuts.

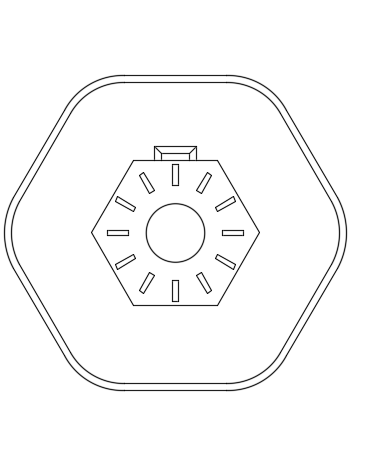
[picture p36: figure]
Line diagram of the tee nut mounting holes on the mounting plate.
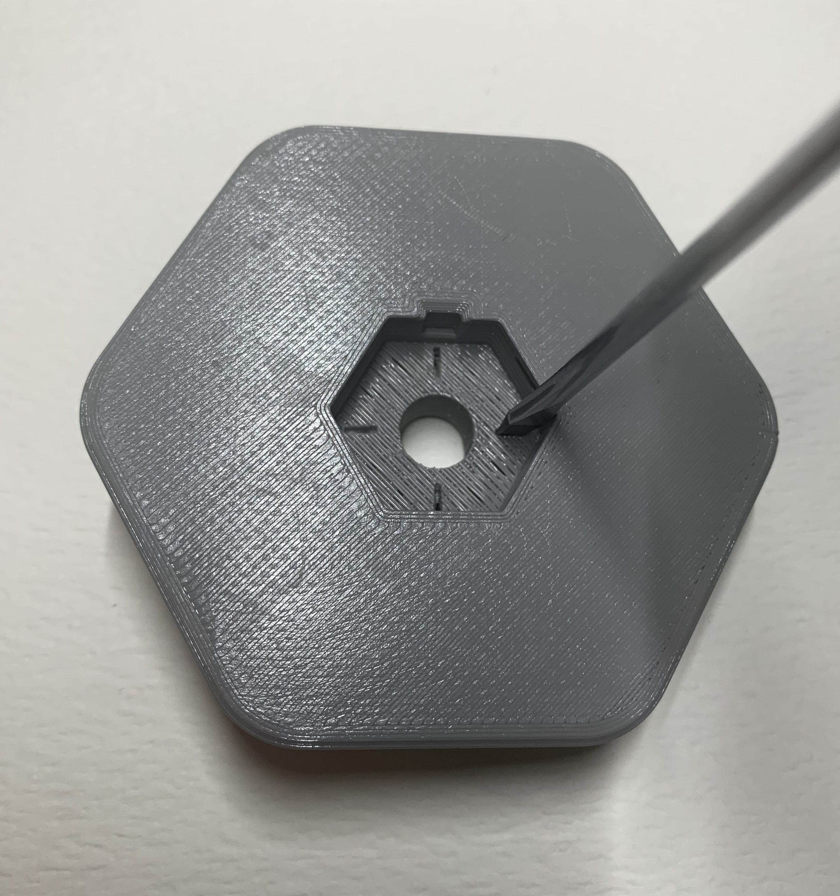
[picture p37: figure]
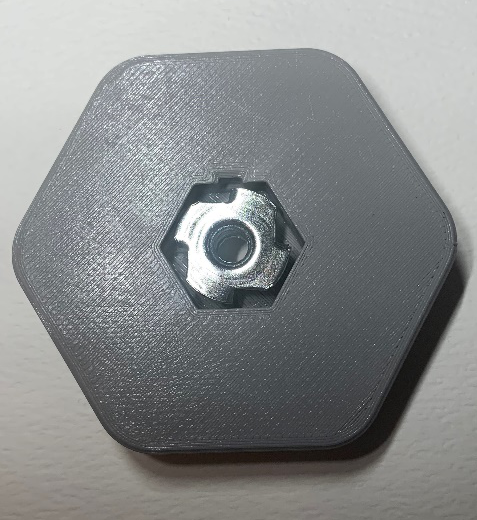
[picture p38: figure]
A tee nut aligned with the mounting holes of the mounting plate.

## Step 2: Install the Tee Nut into the Mounting Plate

With the Tee Nut aligned, firmly press it into the mount until fully seated. A ¼”-20 bolt can be used to help install the tee nut. Place the mounting washer onto the bolt and thread it from the top of the mounting plate and into the tee nut. Tighten the bolt until the tee nut is fully seated. Remove the bolt and discard the washer.

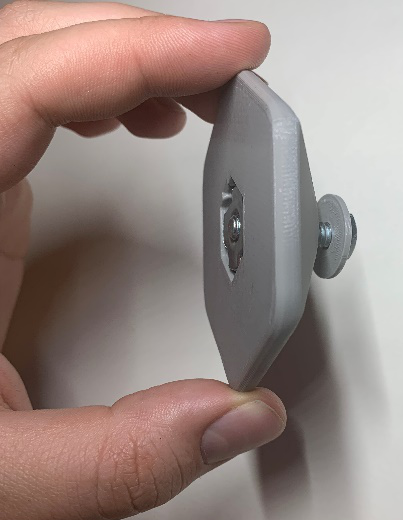
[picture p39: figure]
A hand holding the mounting plate showing a bolt and washer being used to install the tee nut.
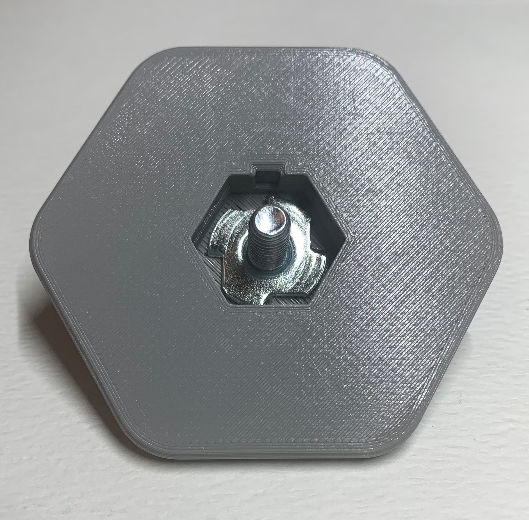
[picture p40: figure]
A bolt being used to fully seat the tee nut into the mounting plate.
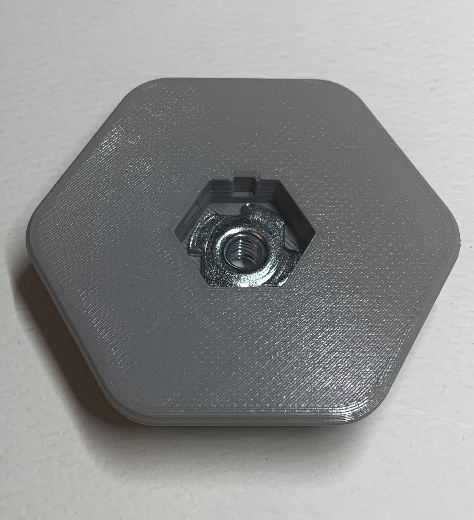
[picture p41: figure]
A tee nut fully installed into the mounting plate.

## Step 3: Install the Hardware Cover

The Hardware Cover must be installed onto the bottom of the mounting plate. Align the hexagonal cover with the hexagonal recess on the mounting plate and firmly press until it snaps into place. Pliers can be used to help insert the cover.

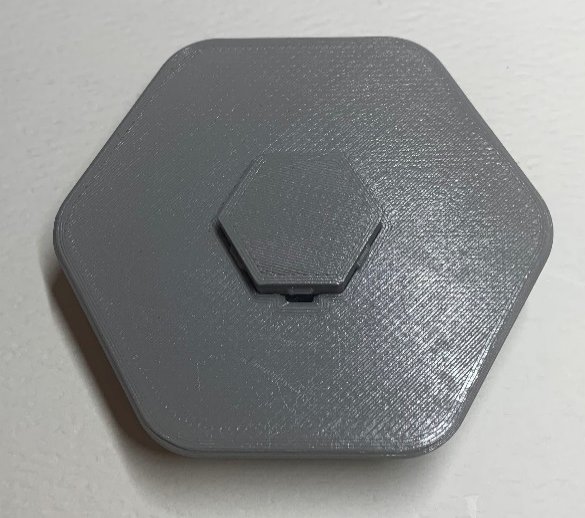
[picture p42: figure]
The hexagonal hardware cover aligned with the hexagonal recess on the mounting plate.
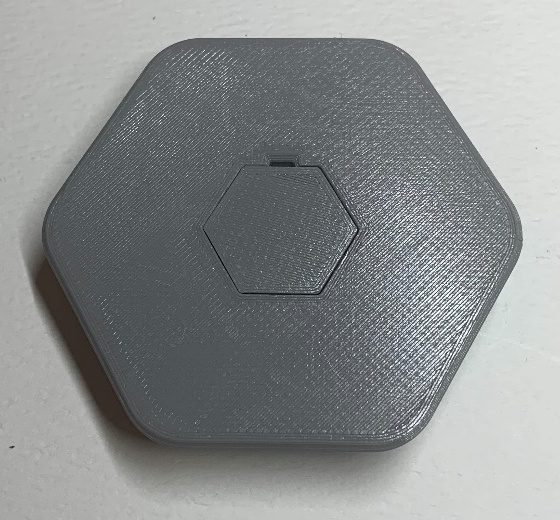
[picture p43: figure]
A fully installed hardware cover sitting flush with the mounting plate surface.

© 2023 by Neil Squire This work is licensed under the CC BY SA 4.0 License: http://creativecommons.org/licenses/by-sa/4.0 Files available at <Replace with MMC Library Link> Page 1 of 1

V1.0 | February 2023 <Device Name> Assembly Guide

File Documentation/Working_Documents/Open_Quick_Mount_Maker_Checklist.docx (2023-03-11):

# Maker To Do List

- Read through the Assembly Guide to become familiar with required components, tools, supplies, and safety gear and overall assembly steps.
- Talk to User about customization options:
  - Mounting Plate Size
  - Print Colour
- Determine the availability of tee nuts.
  - Verify Tee Nut Length using the sizing chart (builder may choose unless the requester has a specific need)
- Order hardware components
- Gather tools, supplies, and safety equipment.
- Assemble the device.
- Test device.
- Print “User Guide”

# Items to Give to User

- Assembled, tested device
- “User Guide”

© 2023 by Neil Squire This work is licensed under the CC BY SA 4.0 License: http://creativecommons.org/licenses/by-sa/4.0 Files available at <Replace with MMC Library Link> Page 1 of 1

V1.0 | February 2023 <Device Name> Maker Checklist

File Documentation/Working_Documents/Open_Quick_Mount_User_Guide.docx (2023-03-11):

## Introduction

The Hexagon Quick Mount is a simple mounting option for assistive devices that do not have integrated mounting hardware. This device uses hook and loop fastener strips to attach to an assistive device allowing it to be mounted with standard ¼”-20 mounts, like those found on readily available camera mounting accessories.

## Features

Mounting Surface

Internal Mounting Threads

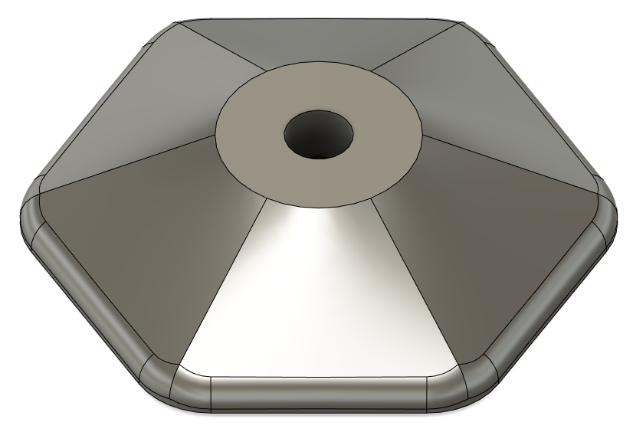
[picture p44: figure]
The front of the mounting plate with a labelled red arrow pointing to the internal mounting threads.
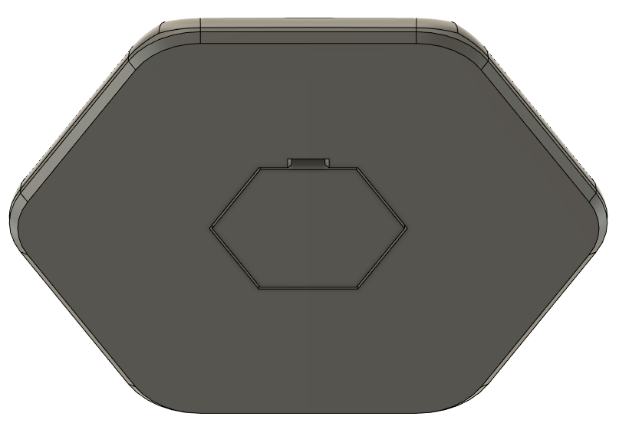
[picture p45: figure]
The bottom of the mounting plate with red arrows pointing to the mounting surface and hardware cover.

Hardware Cover

## Usage

### Attaching Devices

Use hook and loop fastener strips to secure one or more devices to the mounting surface.

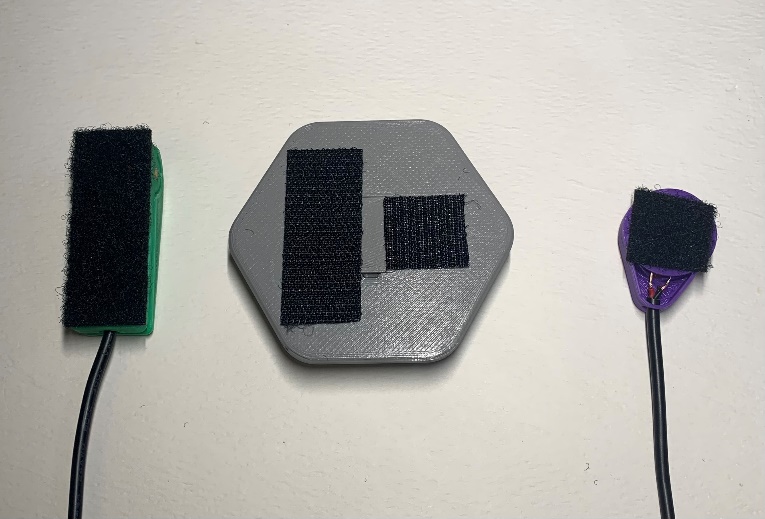
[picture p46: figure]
Velcro strips being added to the mounting plate, a Light Touch switch and a Rain Drop Switch.
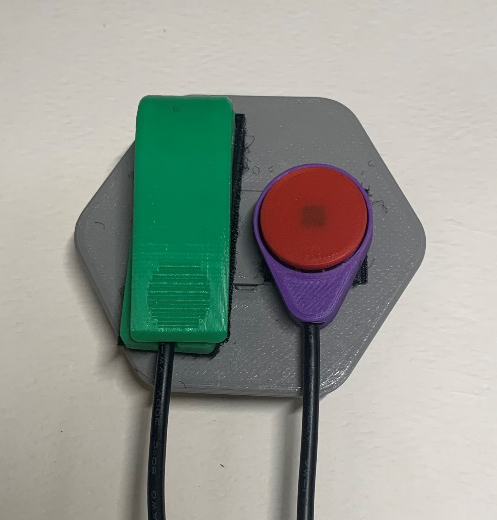
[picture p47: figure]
A Light Touch Switch and a Rain Drop Switch attached to the mounting plate with Velcro.

### Mounting

With your device(s) attached to the mounting surface, thread your mounting system into the internal threads of the mounting plate and lock it in your preferred orientation.

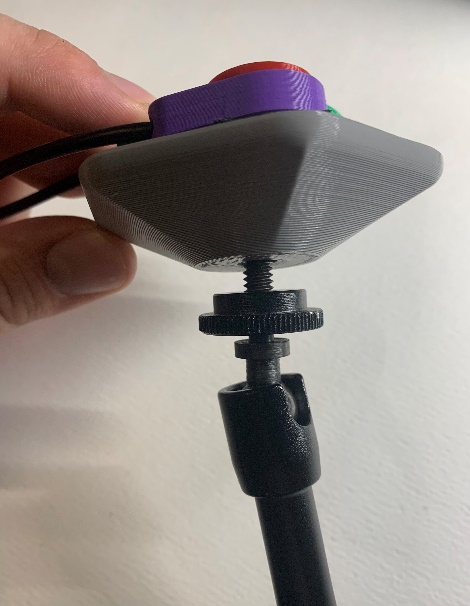
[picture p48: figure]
A hand screwing the mounting plate onto a Magic Arm Mount.
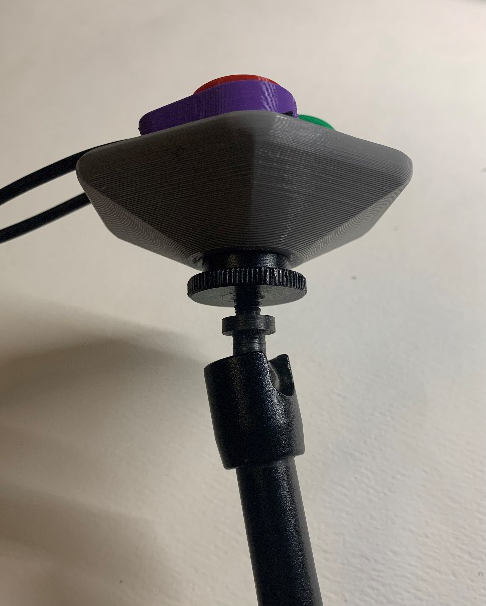
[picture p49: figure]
The mounting plate fully secured to a Magic Arm Mount.
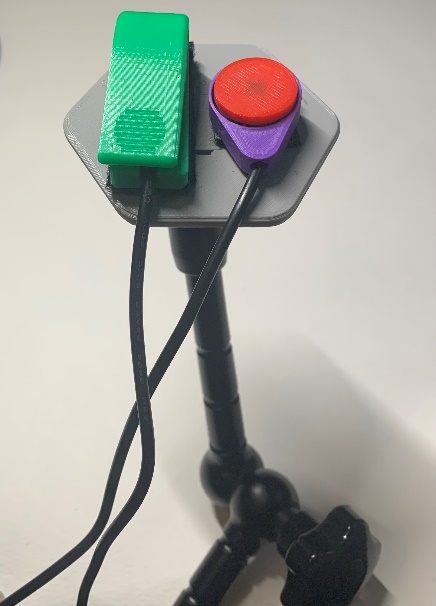
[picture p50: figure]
A Light Touch Switch and Rain Drop Switch secured to the Magic Arm Mount using the mounting plate.

## Compatibility

The mounting plate excepts external ¼” – 20 threads like the ones commonly used in camera mounting systems. There are three available mounting plate sizes that can be selected to match the devices you wish to mount. There are also three options for threaded inserts with 5/16”, 7/16”, and 9/16” lengths of threads. Refer to the Sizing Chart for more information on sizing options.

## Specifications

Mounting Plate | Width [mm] | Length [mm] | Thread Length [mm](in) | Height [mm]
Small_Mounting_Plate_5-16 | 45 | 45 | 7.94 (5/16) | 15.9
Small_Mounting_Plate_7-16 | 65 | 65 | 11.11 (7/16) | 19.1
Small_Mounting_Plate_9-16 | 85 | 85 | 14.29 (9/16) | 22.3
Medium_Mounting_Plate_5-16 | 45 | 45 | 7.94 (5/16) | 15.9
Medium_Mounting_Plate_7-16 | 65 | 65 | 11.11 (7/16) | 19.1
Medium_Mounting_Plate_9-16 | 85 | 85 | 14.29 (9/16) | 22.3
Large_Mounting_Plate_5-16 | 45 | 45 | 7.94 (5/16) | 15.9
Large_Mounting_Plate_7-16 | 65 | 65 | 11.11 (7/16) | 19.1
Large_Mounting_Plate_9-16 | 85 | 85 | 14.29 (9/16) | 22.3

## Cleaning

Wipe with damp cloth or plastic safe cleaning wipes.

© 2023 by Neil Squire. This work is licensed under the CC BY SA 4.0 License: http://creativecommons.org/licenses/by-sa/4.0 Files available at <MMC Project Library Link> Page 2 of 3

V1.0 | February 2023 <Device Name> user Quick Guide

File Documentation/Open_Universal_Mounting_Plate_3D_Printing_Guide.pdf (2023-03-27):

V1.0 | February 2023

## Open Universal Mounting Plate

## 3D PRINTING GUIDE

© 2023 by Neil Squire (https://www.neilsquire.ca/)
This work is licensed under the CC BY SA 4.0 License: http://creativecommons.org/licenses/by-sa/4.0
Files available at https://makersmakingchange.com/project/open-universal-mounting-plate | Page 1 of 5

### Device Variants

This device has three options for mounting plate width and three options for tee nut length. To find accurate print details for each variant, find the corresponding table for your configuration.

### 3D Printing Summary

Configuration | Total Print Time (min) | Total Number of Components | Typical Total Mass (g) | Typical Number of Print Setups
Configuration 1 Small Plate with 5/16” Tee Nut | 84 | 3 | 11 | 1
Configuration 2 Small Plate with 7/16” Tee Nut | 88 | 3 | 12 | 1
Configuration 3 Small Plate with 9/16” Tee Nut | 94 | 3 | 13 | 1
Configuration 4 Medium Plate with 5/16” Tee Nut | 149 | 3 | 19 | 1
Configuration 5 Medium Plate with 7/16” Tee Nut | 143 | 3 | 21 | 1
Configuration 6 Medium Plate with 9/16” Tee Nut | 152 | 3 | 23 | 1
Configuration 7 Large Plate with 5/16” Tee Nut | 214 | 3 | 29 | 1
Configuration 8 Large Plate with 7/16” Tee Nut | 232 | 3 | 32 | 1
Configuration 9 Large Plate with 9/16” Tee Nut | 252 | 3 | 35 | 1

### 3D Printing Settings

### Configuration 1: Small Plate with 5/16” Tee Nut

Print File Name | Qty | Total Print Time (hr:min) | Mass (g) | Infill (%) | Support (Y/N) | Layer Height/ Nozzle Diameter(mm) | Notes (orientation, special settings, etc.)
45_Mounting_Plate_5.stl | 1 | 1:09 | 9 | 20 | N | 0.2/0.4 | Print in orientation given in STL
Hardware_Cover.stl | 1 | 00:10 | 1 | 20 | N | 0.2/0.4 | Print in orientation given in STL
Assembly_Washer.stl (Optional) | 1 | 00:05 | 1 | 20 | N | 0.2/0.4 | Print in orientation given in STL

## 3D PRINTING GUIDE

Files available at https://makersmakingchange.com/project/open-universal-mounting-plate | Page 2 of 5

### Configuration 2: Small Plate with 7/16” Tee Nut

Print File Name | Qty | Total Print Time (hr:min) | Mass (g) | Infill (%) | Support (Y/N) | Layer Height/ Nozzle Diameter(mm) | Notes (orientation, special settings, etc.)
45_Mounting_Plate_7.stl | 1 | 1:13 | 10 | 20 | N | 0.2/0.4 | Print in orientation given in STL
Hardware_Cover.stl | 1 | 00:10 | 1 | 20 | N | 0.2/0.4 | Print in orientation given in STL
Assembly_Washer.stl (Optional) | 1 | 00:05 | 1 | 20 | N | 0.2/0.4 | Print in orientation given in STL

### Configuration 3: Small Plate with 9/16” Tee Nut

Print File Name | Qty | Total Print Time (hr:min) | Mass (g) | Infill (%) | Support (Y/N) | Layer Height/ Nozzle Diameter(mm) | Notes (orientation, special settings, etc.)
45_Mounting_Plate_9.stl | 1 | 1:19 | 11 | 20 | N | 0.2/0.4 | Print in orientation given in STL
Hardware_Cover.stl | 1 | 00:10 | 1 | 20 | N | 0.2/0.4 | Print in orientation given in STL
Assembly_Washer.stl (Optional) | 1 | 00:05 | 1 | 20 | N | 0.2/0.4 | Print in orientation given in STL

### Configuration 4: Medium Plate with 5/16” Tee Nut

Print File Name | Qty | Total Print Time (hr:min) | Mass (g) | Infill (%) | Support (Y/N) | Layer Height/ Nozzle Diameter(mm) | Notes (orientation, special settings, etc.)
65_Mounting_Plate_5.stl | 1 | 2:14 | 17 | 20 | N | 0.2/0.4 | Print in orientation given in STL
Hardware_Cover.stl | 1 | 00:10 | 1 | 20 | N | 0.2/0.4 | Print in orientation given in STL
Assembly_Washer.stl (Optional) | 1 | 00:05 | 1 | 20 | N | 0.2/0.4 | Print in orientation given in STL

### Configuration 5: Medium Plate with 7/16” Tee Nut

Print File Name | Qty | Total Print Time (hr:min) | Mass (g) | Infill (%) | Support (Y/N) | Layer Height/ Nozzle Diameter(mm) | Notes (orientation, special settings, etc.)
65_Mounting_Plate_7.stl | 1 | 2:08 | 19 | 20 | N | 0.2/0.4 | Print in orientation given in STL
Hardware_Cover.stl | 1 | 00:10 | 1 | 20 | N | 0.2/0.4 | Print in orientation given in STL
Assembly_Washer.stl (Optional) | 1 | 00:05 | 1 | 20 | N | 0.2/0.4 | Print in orientation given in STL

## 3D PRINTING GUIDE

Files available at https://makersmakingchange.com/project/open-universal-mounting-plate | Page 3 of 5

### Configuration 6: Medium Plate with 9/16” Tee Nut

Print File Name | Qty | Total Print Time (hr:min) | Mass (g) | Infill (%) | Support (Y/N) | Layer Height/ Nozzle Diameter(mm) | Notes (orientation, special settings, etc.)
65_Mounting_Plate_9.stl | 1 | 2:17 | 21 | 20 | N | 0.2/0.4 | Print in orientation given in STL
Hardware_Cover.stl | 1 | 00:10 | 1 | 20 | N | 0.2/0.4 | Print in orientation given in STL
Assembly_Washer.stl (Optional) | 1 | 00:05 | 1 | 20 | N | 0.2/0.4 | Print in orientation given in STL

### Configuration 7: Large Plate with 5/16” Tee Nut

Print File Name | Qty | Total Print Time (hr:min) | Mass (g) | Infill (%) | Support (Y/N) | Layer Height/ Nozzle Diameter(mm) | Notes (orientation, special settings, etc.)
85_Mounting_Plate_5.stl | 1 | 3:19 | 27 | 20 | N | 0.2/0.4 | Print in orientation given in STL
Hardware_Cover.stl | 1 | 00:10 | 1 | 20 | N | 0.2/0.4 | Print in orientation given in STL
Assembly_Washer.stl (Optional) | 1 | 00:05 | 1 | 20 | N | 0.2/0.4 | Print in orientation given in STL

### Configuration 8: Large Plate with 7/16” Tee Nut

Print File Name | Qty | Total Print Time (hr:min) | Mass (g) | Infill (%) | Support (Y/N) | Layer Height/ Nozzle Diameter(mm) | Notes (orientation, special settings, etc.)
85_Mounting_Plate_7.stl | 1 | 3:37 | 30 | 20 | N | 0.2/0.4 | Print in orientation given in STL
Hardware_Cover.stl | 1 | 00:10 | 1 | 20 | N | 0.2/0.4 | Print in orientation given in STL
Assembly_Washer.stl (Optional) | 1 | 00:05 | 1 | 20 | N | 0.2/0.4 | Print in orientation given in STL

### Configuration 9: Large Plate with 9/16” Tee Nut

Print File Name | Qty | Total Print Time (hr:min) | Mass (g) | Infill (%) | Support (Y/N) | Layer Height/ Nozzle Diameter(mm) | Notes (orientation, special settings, etc.)
85_Mounting_Plate_9.stl | 1 | 3:57 | 33 | 20 | N | 0.2/0.4 | Print in orientation given in STL
Hardware_Cover.stl | 1 | 00:10 | 1 | 20 | N | 0.2/0.4 | Print in orientation given in STL
Assembly_Washer.stl (Optional) | 1 | 00:05 | 1 | 20 | N | 0.2/0.4 | Print in orientation given in STL

## 3D PRINTING GUIDE

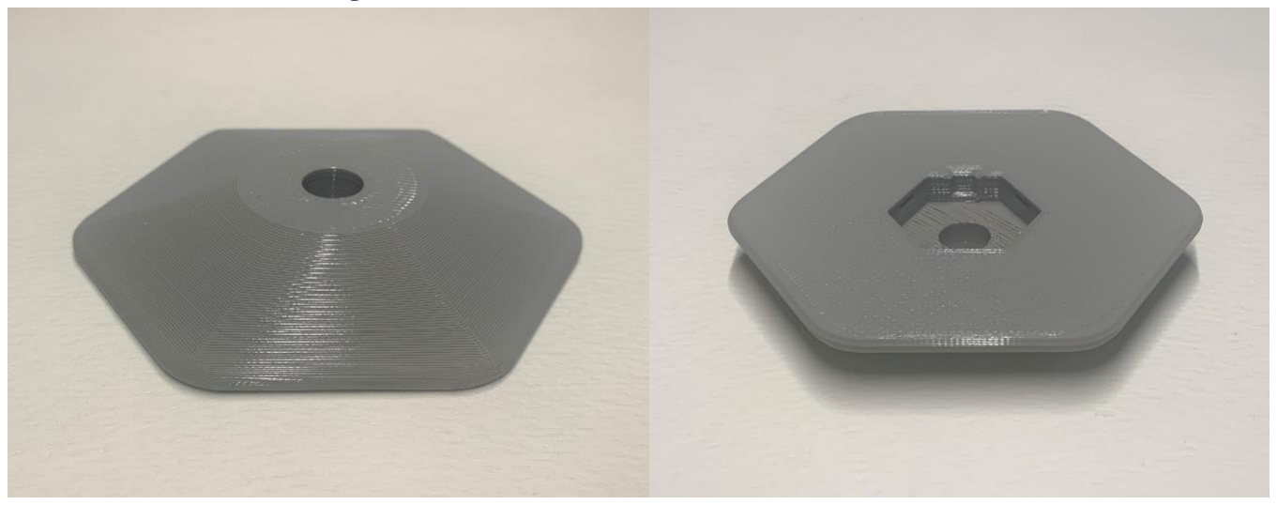
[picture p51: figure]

Files available at https://makersmakingchange.com/project/open-universal-mounting-plate | Page 4 of 5

### Post-Processing

The mounting plate has a sacrificial bridge across tee nut mount that must be removed. Use pliers to clear this and any other loose print material. All parts should be inspected to ensure that all surfaces are smooth, and edges are non-sharp.

### Customization Options

Users may request their choice print colour and mounting plate size from small, medium, and large. There are also three variants of tee nut sizes to match the hardware the builder chooses to use. Use the Sizing Diagram to verify what size tee nut you are using and select the corresponding STL file for the mounting plate.

### Custom Hardware

Print files have been released for 3 mounting plate sizes with 3 tee nut sizes each, but custom hardware and sizes can also be implemented. A parametric Fusion 360 model is available that can be adjusted to make custom mounting plates.

### Examples of Quality Prints

### Photos of the Mounting Plate

Note: This is an example of one of the nine total options of the mounting plate.

## 3D PRINTING GUIDE

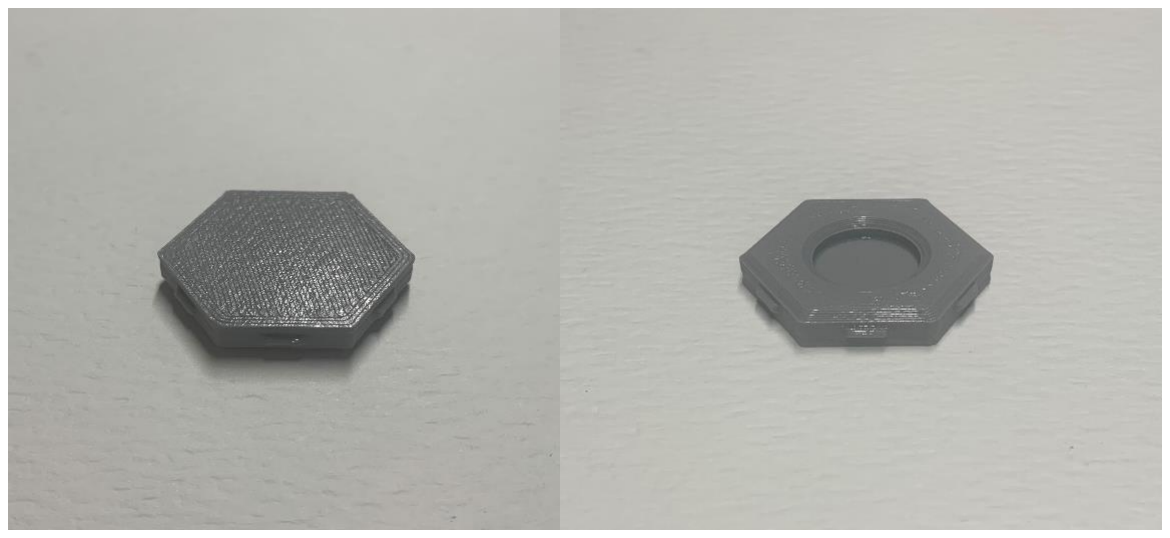
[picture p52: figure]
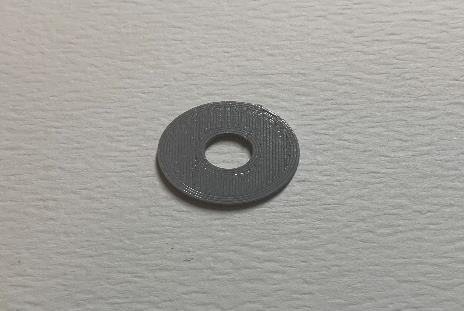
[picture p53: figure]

Files available at https://makersmakingchange.com/project/open-universal-mounting-plate | Page 5 of 5

### Photos of the Hardware Cover

### Photos of the Assembly Washer

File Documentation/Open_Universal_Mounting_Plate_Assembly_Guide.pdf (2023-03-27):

V1.0 | February 2023

## Open Universal Mounting Plate

## ASSEMBLY GUIDE

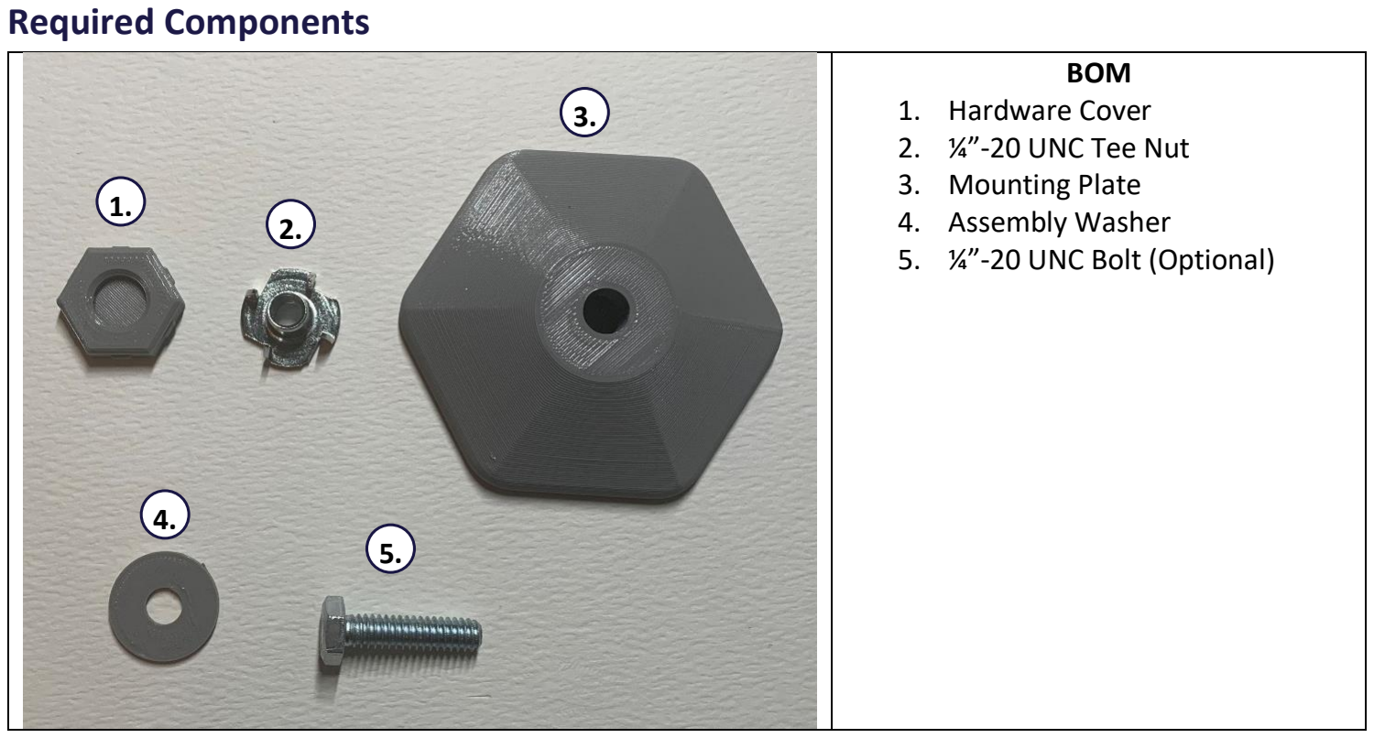
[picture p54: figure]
Required Components; BOM 1. Hardware Cover 2. ¼”-20 UNC Tee Nut 3. Mounting Plate 4. Assembly Washer 5. ¼”-20 UNC Bolt (Optional)

© 2023 by Neil Squire (https://neilsquire.ca/)
This work is licensed under the CC BY SA 4.0 License: http://creativecommons.org/licenses/by-sa/4.0
Files available at Files available at https://makersmakingchange.com/project/open-universal-mounting-plate | Page 1 of 3

Required Tools

- Pliers
- Small Flat Head Screwdriver

Required Personal Protective Equipment (PPE)

- Safety Glasses

## ASSEMBLY GUIDE

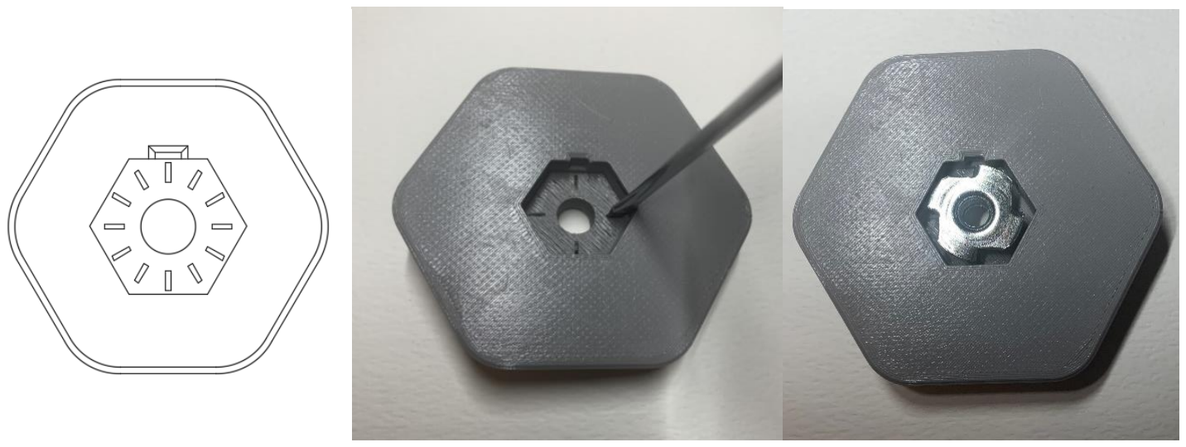
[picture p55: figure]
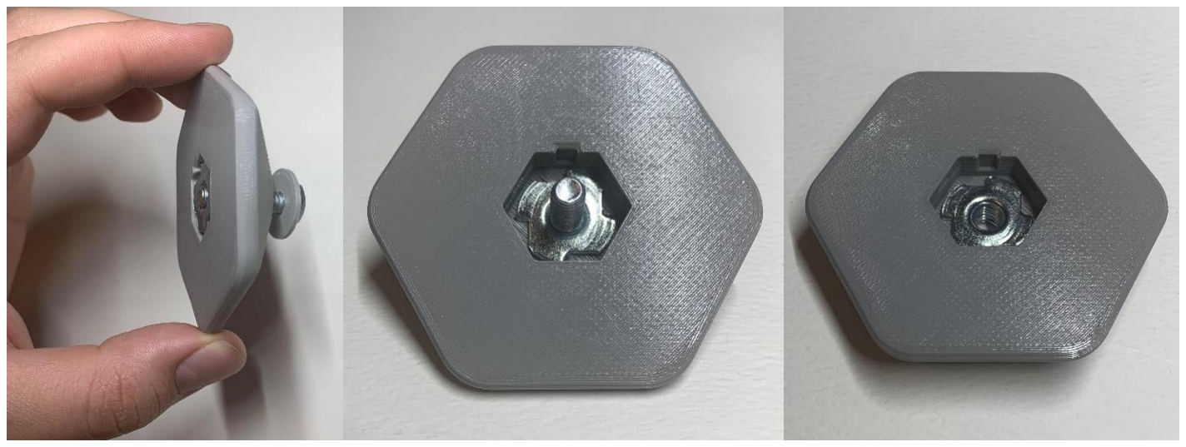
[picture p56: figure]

Files available at Files available at https://makersmakingchange.com/project/open-universal-mounting-plate | Page 2 of 3

Mounting Plate Assembly Instructions

Step 1: Align the Tee Nut
Align the prongs of the Tee Nut with their corresponding holes in the mounting plate. These holes may be covered by the sacrificial bridge used for printing, so a small flathead screwdriver can be used to pierce the mounting holes to make it easier to install.

Note: There are mounting holes for three-, four-, and six-pronged Tee Nuts.

Step 2: Install the Tee Nut into the Mounting Plate
With the Tee Nut aligned, firmly press it into the mount until fully seated. A ¼”-20 bolt can be used to help install the tee nut. Place the mounting washer onto the bolt and thread it from the top of the mounting plate and into the tee nut. Tighten the bolt until the tee nut is fully seated. Remove the bolt and discard the washer.

## ASSEMBLY GUIDE

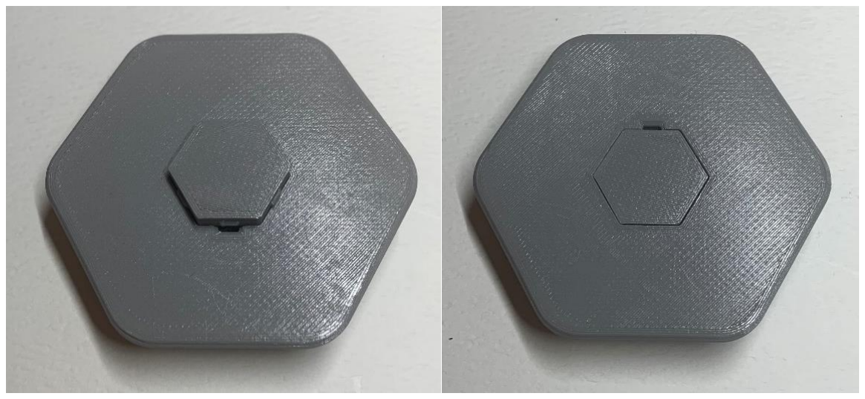
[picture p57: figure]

Files available at Files available at https://makersmakingchange.com/project/open-universal-mounting-plate | Page 3 of 3
Step 3: Install the Hardware Cover
The Hardware Cover must be installed onto the bottom of the mounting plate. Align the hexagonal cover with the hexagonal recess on the mounting plate and firmly press until it snaps into place. Pliers can be used to help insert the cover.

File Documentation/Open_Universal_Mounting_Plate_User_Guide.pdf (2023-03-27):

V1.0 | February 2023

## Open Universal Mounting Plate

## USER QUICK GUIDE

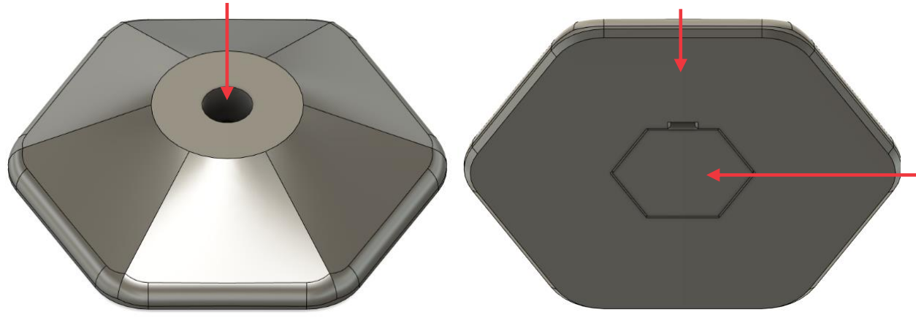
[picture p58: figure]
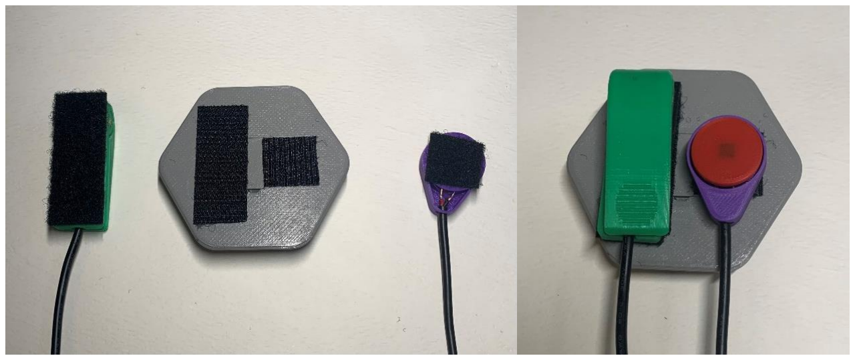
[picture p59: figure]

© 2023 by Neil Squire. (https://neilsquire.ca/)
This work is licensed under the CC BY SA 4.0 License: http://creativecommons.org/licenses/by-sa/4.0 Files available at https://makersmakingchange.com/project/open-universal-mounting-plate

### Introduction

The Open Universal Mounting Plate is a simple mounting option for assistive devices that do not have integrated mounting hardware. This device uses hook and loop fastener strips to attach to an assistive device allowing it to be mounted with standard ¼”-20 mounts, like those found on readily available camera mounting accessories.

### Features

### Usage

Attaching Devices
Use hook and loop fastener strips to secure one or more devices to the mounting surface.

Internal Mounting
Threads

Mounting
Surface

Hardware
Cover

V1.0 | February 2023

## Open Universal Mounting Plate

## USER QUICK GUIDE

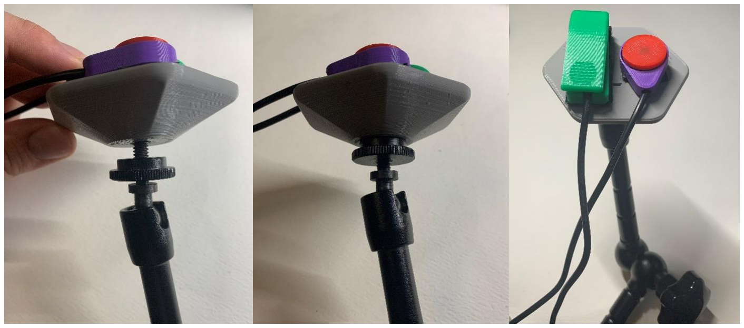
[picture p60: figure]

© 2023 by Neil Squire. (https://neilsquire.ca/)
This work is licensed under the CC BY SA 4.0 License: http://creativecommons.org/licenses/by-sa/4.0 Files available at https://makersmakingchange.com/project/open-universal-mounting-plate

Mounting
With your device(s) attached to the mounting surface, thread your mounting system into the internal threads of the mounting plate and lock it in your preferred orientation.

### Compatibility

The mounting plate excepts external ¼” – 20 threads like the ones commonly used in camera mounting systems. There are three available mounting plate sizes that can be selected to match the devices you wish to mount. There are also three options for threaded inserts with 5/16”, 7/16”, and 9/16” lengths of threads. Refer to the Sizing Chart for more information on sizing options.

### Specifications

Mounting Plate | Width [mm] | Length [mm] | Thread Length [mm](in) | Height [mm]
Small_Mounting_Plate_5-16 | 45 | 45 | 7.94 (5/16) | 15.9
Small_Mounting_Plate_7-16 | 65 | 65 | 11.11 (7/16) | 19.1
Small_Mounting_Plate_9-16 | 85 | 85 | 14.29 (9/16) | 22.3
Medium_Mounting_Plate_5-16 | 45 | 45 | 7.94 (5/16) | 15.9
Medium_Mounting_Plate_7-16 | 65 | 65 | 11.11 (7/16) | 19.1
Medium_Mounting_Plate_9-16 | 85 | 85 | 14.29 (9/16) | 22.3
Large_Mounting_Plate_5-16 | 45 | 45 | 7.94 (5/16) | 15.9
Large_Mounting_Plate_7-16 | 65 | 65 | 11.11 (7/16) | 19.1
Large_Mounting_Plate_9-16 | 85 | 85 | 14.29 (9/16) | 22.3

### Cleaning

Wipe with damp cloth or plastic safe cleaning wipes.

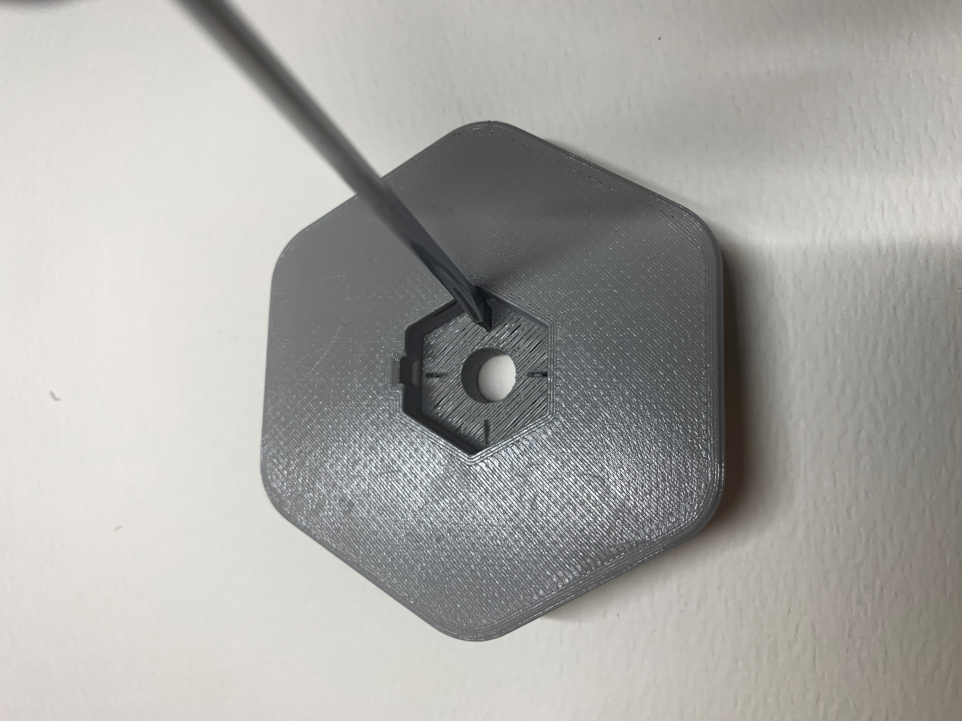
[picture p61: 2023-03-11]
Photos/Assembly_Photos/Clearing_Holes_for_Tee_Nut.jpg

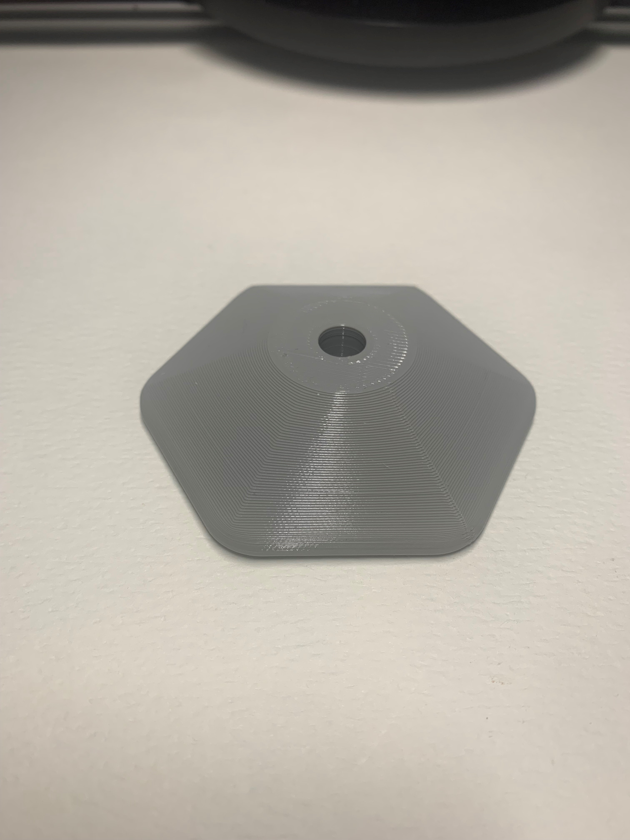
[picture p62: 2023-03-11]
Photos/Print_Photos/Mounting_Plate_Back.jpg

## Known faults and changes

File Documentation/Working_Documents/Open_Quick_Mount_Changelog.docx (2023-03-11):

# Version 1.0 | 2023/02/14

- A simple mounting option for AT without integrated mounting hardware.
- Attaches to AT with hook and loop fastener strips.
- Supplies internal ¼"-20 UNC threads for mounting.
- Parametric model that can be customized for any hardware and plate size.
- Design and documentation by Makers Making Change.

© 2023 by Neil Squire This work is licensed under the CC BY SA 4.0 License: http://creativecommons.org/licenses/by-sa/4.0 Files available at <Replace with MMC Library Link> Page 1 of 1

V1.0 | February 2023 <Device Name> changelog
